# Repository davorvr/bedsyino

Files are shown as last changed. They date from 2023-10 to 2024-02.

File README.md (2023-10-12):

# BeDSyino

#### What is it?

The **[BeDSy (Behaviour-recording Device Synchroniser)](https://github.com/davorvr/bedsy)** is a platform for hardware triggering and synchronisation of equipment for laboratory animal behavioural monitoring. For more information about the BeDSy platform, check the **[BeDSy repository](https://github.com/davorvr/bedsy)**.

The platform consists of two components: the **[BeDSy Python package](https://github.com/davorvr/bedsy)**, which interfaces with the **BeDSyino**, a hardware platform which sends custom trigger signals to animal behaviour-monitoring devices.

The BeDSyino is based on the [Teensy 4.0](https://www.pjrc.com/store/teensy40.html) platform (with plans to migrate to the Teensy 4.1) and [Teensyduino](https://www.pjrc.com/teensy/teensyduino.html).

#### Current state

The [BeDSyino](https://github.com/davorvr/bedsyino) is still cooking. While the code is mostly complete, only a single hand-soldered, protoboard-based prototype has been developed thus far. A modular, extensible hardware platform is currently in the works and hardware files will be uploaded as soon as it's ready. The `.ino` file contains a lot of (hopefully) helpful comments, but more work on the documentation is necessary.

*TO DO - expand*

#### License

The code is distributed under GPLv3.

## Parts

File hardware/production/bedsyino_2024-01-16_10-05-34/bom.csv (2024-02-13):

Designator | Footprint | Quantity | Value | LCSC Part #
C1 | 1206 | 1 | 10uF | C97954
C2, C3, C4, C5, C6 | 0805 | 5 | 0.1uF | C49678
R1, R10, R2, R3, R4, R5, R6, R7, R8, R9 | 0805 | 10 | 10k | C100047
U2 | SOIC-20W_7.5x12.8mm_P1.27mm | 1 | CD74HCT241M96 | C2860724
U3, U4, U5, U6 | SOIC8-N_MC_MCH | 4 | TC4427AVOA | C624944

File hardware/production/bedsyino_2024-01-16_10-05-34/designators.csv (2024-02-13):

C1:1
C2:1
C3:1
C4:1
C5:1
C6:1
J1:1
J10:1
J11:1
J2:1
J3:1
J4:1
J5:1
J6:1
J7:1
J8:1
J9:1
JP1:1
JP10:1
JP11:1
JP12:1
JP13:1
JP14:1
JP15:1
JP16:1
JP17:1
JP18:1
JP19:1
JP2:1
JP20:1
JP21:1
JP22:1
JP23:1
JP24:1
JP25:1
JP26:1
JP27:1
JP28:1
JP3:1
JP4:1
JP5:1
JP6:1
JP7:1
JP8:1
JP9:1
R1:1
R10:1
R2:1
R3:1
R4:1
R5:1
R6:1
R7:1
R8:1
R9:1
REF**:3
U1:1
U2:1
U3:1
U4:1
U5:1
U6:1

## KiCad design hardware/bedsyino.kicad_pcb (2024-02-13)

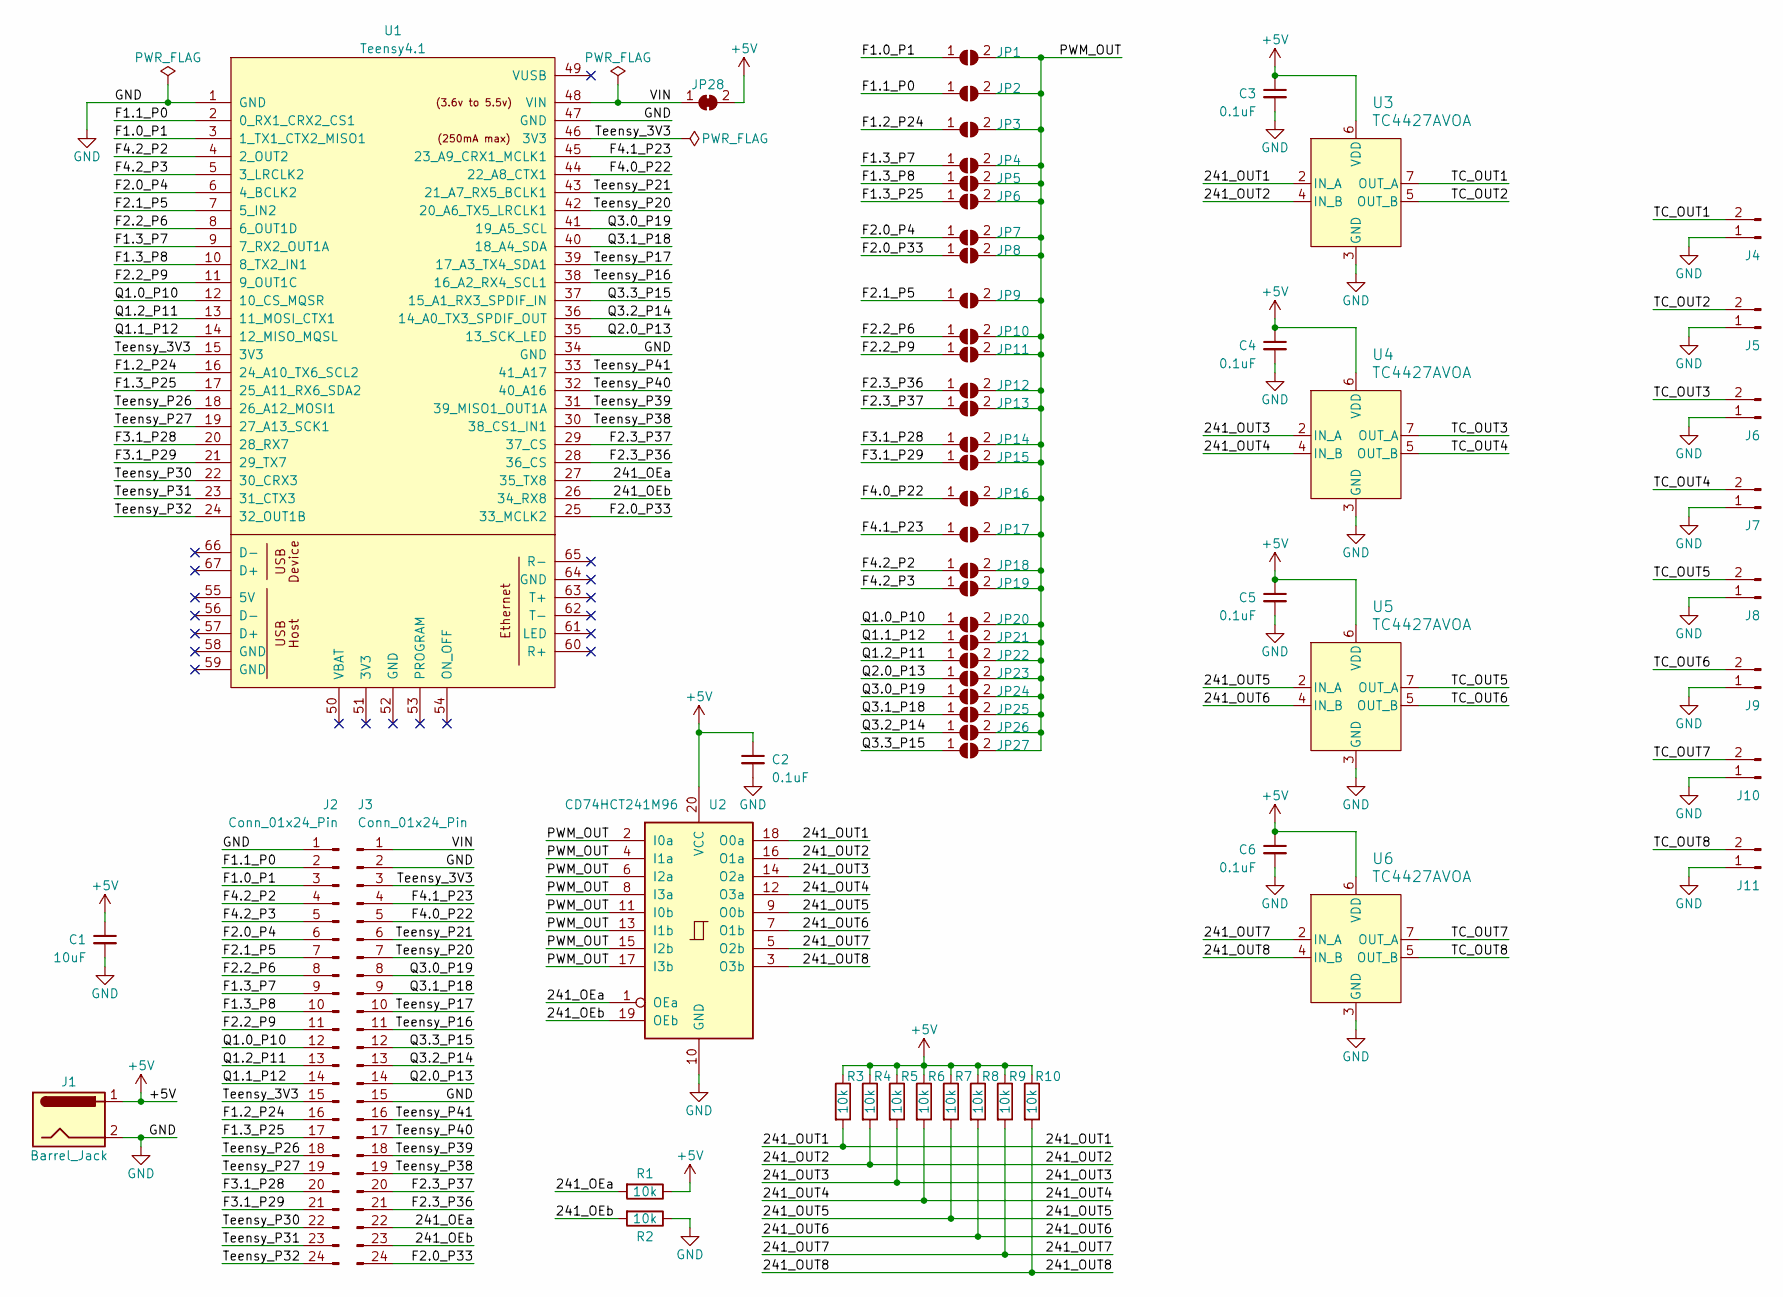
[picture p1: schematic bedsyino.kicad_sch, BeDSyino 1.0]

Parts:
C1: 10uF; C_1206_3216Metric; LCSC Part # C97954
C2, C3, C4, C5, C6: 0.1uF; C_0805_2012Metric; LCSC Part # C49678
J1: Barrel_Jack; BarrelJack_Horizontal
J2, J3: Conn_01x24_Pin; PinHeader_1x24_P2.54mm_Vertical
J4, J5, J6, J7, J8, J9, J10, J11: Conn_01x02_Pin; Molex_KK-254_AE-7395-02_1x02_P2.54mm_Horizontal
JP1: F1.0 P1; SolderJumper-2_P1.3mm_Open_TrianglePad1.0x1.5mm
JP2: F1.1 P0; SolderJumper-2_P1.3mm_Open_TrianglePad1.0x1.5mm
JP3: F1.2 P24; SolderJumper-2_P1.3mm_Open_TrianglePad1.0x1.5mm
JP4: F1.3 P7; SolderJumper-2_P1.3mm_Open_TrianglePad1.0x1.5mm
JP5: F1.3 P8; SolderJumper-2_P1.3mm_Open_TrianglePad1.0x1.5mm
JP6: F1.3 P25; SolderJumper-2_P1.3mm_Open_TrianglePad1.0x1.5mm
JP7: F2.0 P4; SolderJumper-2_P1.3mm_Open_TrianglePad1.0x1.5mm
JP8: F2.0 P33; SolderJumper-2_P1.3mm_Open_TrianglePad1.0x1.5mm
JP9: F2.1 P5; SolderJumper-2_P1.3mm_Open_TrianglePad1.0x1.5mm
JP10: F2.2 P6; SolderJumper-2_P1.3mm_Open_TrianglePad1.0x1.5mm
JP11: F2.2 P9; SolderJumper-2_P1.3mm_Open_TrianglePad1.0x1.5mm
JP12: F2.3 P36; SolderJumper-2_P1.3mm_Open_TrianglePad1.0x1.5mm
JP13: F2.3 P37; SolderJumper-2_P1.3mm_Open_TrianglePad1.0x1.5mm
JP14: F3.1 P28; SolderJumper-2_P1.3mm_Open_TrianglePad1.0x1.5mm
JP15: F3.1 P29; SolderJumper-2_P1.3mm_Open_TrianglePad1.0x1.5mm
JP16: F4.0 P22; SolderJumper-2_P1.3mm_Open_TrianglePad1.0x1.5mm
JP17: F4.1 P23; SolderJumper-2_P1.3mm_Open_TrianglePad1.0x1.5mm
JP18: F4.2 P2; SolderJumper-2_P1.3mm_Open_TrianglePad1.0x1.5mm
JP19: F4.2 P3; SolderJumper-2_P1.3mm_Open_TrianglePad1.0x1.5mm
JP20: Q1.0 P10; SolderJumper-2_P1.3mm_Open_TrianglePad1.0x1.5mm
JP21: Q1.1 P12; SolderJumper-2_P1.3mm_Open_TrianglePad1.0x1.5mm
JP22: Q1.2 P11; SolderJumper-2_P1.3mm_Open_TrianglePad1.0x1.5mm
JP23: Q2.0 P13; SolderJumper-2_P1.3mm_Open_TrianglePad1.0x1.5mm
JP24: Q3.0 P19; SolderJumper-2_P1.3mm_Open_TrianglePad1.0x1.5mm
JP25: Q3.1 P18; SolderJumper-2_P1.3mm_Open_TrianglePad1.0x1.5mm
JP26: Q3.2 P14; SolderJumper-2_P1.3mm_Open_TrianglePad1.0x1.5mm
JP27: Q3.3 P15; SolderJumper-2_P1.3mm_Open_TrianglePad1.0x1.5mm
JP28: PWR SELECT; SolderJumper-2_P1.3mm_Bridged2Bar_Pad1.0x1.5mm
R1, R2, R3, R4, R5, R6, R7, R8, R9, R10: 10k; R_0805_2012Metric; LCSC Part # C100047
U1: Teensy4.1; Teensy41
U2: CD74HCT241M96; SOIC-20W_7.5x12.8mm_P1.27mm; LCSC Part # C2860724
U3, U4, U5, U6: TC4427AVOA; SOIC8-N_MC_MCH; LCSC Part # C624944

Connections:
+5V: C1.1, C2.1, C3.1, C4.1, C5.1, C6.1, J1.1, JP28.2 (B), R1.1, R3.1, R4.1, R5.1, R6.1, R7.1, R8.1, R9.1, R10.1, U2.20 (VCC), U3.6 (VDD), U4.6 (VDD), U5.6 (VDD), U6.6 (VDD)
/241_OEa: J3.22, R1.2, U1.27 (35_TX8), U2.1 (OEa)
/241_OEb: J3.23, R2.2, U1.26 (34_RX8), U2.19 (OEb)
/241_OUT1: R3.2, U2.18 (O0a), U3.2 (IN_A)
/241_OUT2: R4.2, U2.16 (O1a), U3.4 (IN_B)
/241_OUT3: R5.2, U2.14 (O2a), U4.2 (IN_A)
/241_OUT4: R6.2, U2.12 (O3a), U4.4 (IN_B)
/241_OUT5: R7.2, U2.9 (O0b), U5.2 (IN_A)
/241_OUT6: R8.2, U2.7 (O1b), U5.4 (IN_B)
/241_OUT7: R9.2, U2.5 (O2b), U6.2 (IN_A)
/241_OUT8: R10.2, U2.3 (O3b), U6.4 (IN_B)
/F1.0_P1: J2.3, JP1.1 (A), U1.3 (1_TX1_CTX2_MISO1)
/F1.1_P0: J2.2, JP2.1 (A), U1.2 (0_RX1_CRX2_CS1)
/F1.2_P24: J2.16, JP3.1 (A), U1.16 (24_A10_TX6_SCL2)
/F1.3_P7: J2.9, JP4.1 (A), U1.9 (7_RX2_OUT1A)
/F1.3_P8: J2.10, JP5.1 (A), U1.10 (8_TX2_IN1)
/F1.3_P25: J2.17, JP6.1 (A), U1.17 (25_A11_RX6_SDA2)
/F2.0_P4: J2.6, JP7.1 (A), U1.6 (4_BCLK2)
/F2.0_P33: J3.24, JP8.1 (A), U1.25 (33_MCLK2)
/F2.1_P5: J2.7, JP9.1 (A), U1.7 (5_IN2)
/F2.2_P6: J2.8, JP10.1 (A), U1.8 (6_OUT1D)
/F2.2_P9: J2.11, JP11.1 (A), U1.11 (9_OUT1C)
/F2.3_P36: J3.21, JP12.1 (A), U1.28 (36_CS)
/F2.3_P37: J3.20, JP13.1 (A), U1.29 (37_CS)
/F3.1_P28: J2.20, JP14.1 (A), U1.20 (28_RX7)
/F3.1_P29: J2.21, JP15.1 (A), U1.21 (29_TX7)
/F4.0_P22: J3.5, JP16.1 (A), U1.44 (22_A8_CTX1)
/F4.1_P23: J3.4, JP17.1 (A), U1.45 (23_A9_CRX1_MCLK1)
/F4.2_P2: J2.4, JP18.1 (A), U1.4 (2_OUT2)
/F4.2_P3: J2.5, JP19.1 (A), U1.5 (3_LRCLK2)
/PWM_OUT: JP1.2 (B), JP2.2 (B), JP3.2 (B), JP4.2 (B), JP5.2 (B), JP6.2 (B), JP7.2 (B), JP8.2 (B), JP9.2 (B), JP10.2 (B), JP11.2 (B), JP12.2 (B), JP13.2 (B), JP14.2 (B), JP15.2 (B), JP16.2 (B), JP17.2 (B), JP18.2 (B), JP19.2 (B), JP20.2 (B), JP21.2 (B), JP22.2 (B), JP23.2 (B), JP24.2 (B), JP25.2 (B), JP26.2 (B), JP27.2 (B), U2.2 (I0a), U2.4 (I1a), U2.6 (I2a), U2.8 (I3a), U2.11 (I0b), U2.13 (I1b), U2.15 (I2b), U2.17 (I3b)
/Q1.0_P10: J2.12, JP20.1 (A), U1.12 (10_CS_MQSR)
/Q1.1_P12: J2.14, JP21.1 (A), U1.14 (12_MISO_MQSL)
/Q1.2_P11: J2.13, JP22.1 (A), U1.13 (11_MOSI_CTX1)
/Q2.0_P13: J3.14, JP23.1 (A), U1.35 (13_SCK_LED)
/Q3.0_P19: J3.8, JP24.1 (A), U1.41 (19_A5_SCL)
/Q3.1_P18: J3.9, JP25.1 (A), U1.40 (18_A4_SDA)
/Q3.2_P14: J3.13, JP26.1 (A), U1.36 (14_A0_TX3_SPDIF_OUT)
/Q3.3_P15: J3.12, JP27.1 (A), U1.37 (15_A1_RX3_SPDIF_IN)
/TC_OUT1: J4.2, U3.7 (OUT_A)
/TC_OUT2: J5.2, U3.5 (OUT_B)
/TC_OUT3: J6.2, U4.7 (OUT_A)
/TC_OUT4: J7.2, U4.5 (OUT_B)
/TC_OUT5: J8.2, U5.7 (OUT_A)
/TC_OUT6: J9.2, U5.5 (OUT_B)
/TC_OUT7: J10.2, U6.7 (OUT_A)
/TC_OUT8: J11.2, U6.5 (OUT_B)
/Teensy_3V3: J2.15, J3.3, U1.15 (3V3), U1.46 (3V3)
/Teensy_P16: J3.11, U1.38 (16_A2_RX4_SCL1)
/Teensy_P17: J3.10, U1.39 (17_A3_TX4_SDA1)
/Teensy_P20: J3.7, U1.42 (20_A6_TX5_LRCLK1)
/Teensy_P21: J3.6, U1.43 (21_A7_RX5_BCLK1)
/Teensy_P26: J2.18, U1.18 (26_A12_MOSI1)
/Teensy_P27: J2.19, U1.19 (27_A13_SCK1)
/Teensy_P30: J2.22, U1.22 (30_CRX3)
/Teensy_P31: J2.23, U1.23 (31_CTX3)
/Teensy_P32: J2.24, U1.24 (32_OUT1B)
/Teensy_P38: J3.19, U1.30 (38_CS1_IN1)
/Teensy_P39: J3.18, U1.31 (39_MISO1_OUT1A)
/Teensy_P40: J3.17, U1.32 (40_A16)
/Teensy_P41: J3.16, U1.33 (41_A17)
/VIN: J3.1, JP28.1 (A), U1.48 (VIN)
GND: C1.2, C2.2, C3.2, C4.2, C5.2, C6.2, J1.2, J2.1, J3.2, J3.15, J4.1, J5.1, J6.1, J7.1, J8.1, J9.1, J10.1, J11.1, R2.1, U1.1 (GND), U1.34 (GND), U1.47 (GND), U2.10 (GND), U3.3 (GND), U4.3 (GND), U5.3 (GND), U6.3 (GND)

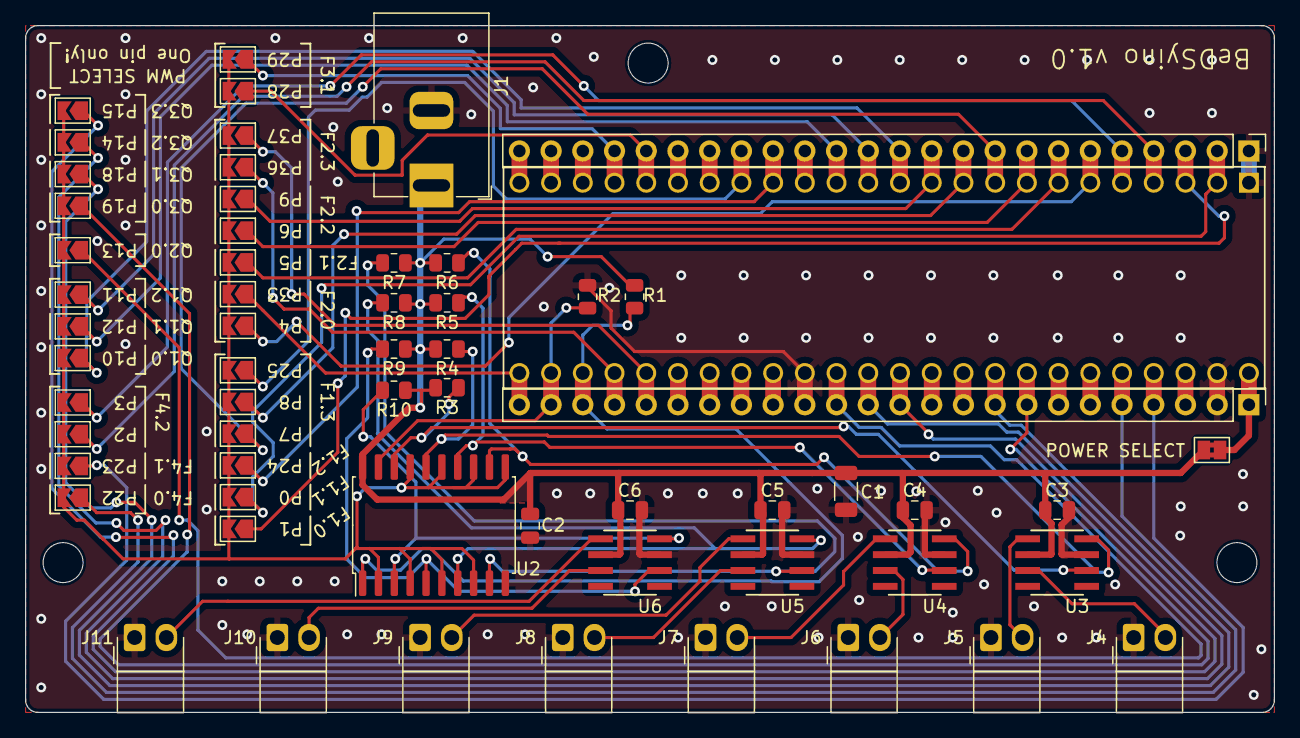
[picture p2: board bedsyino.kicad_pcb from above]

Board: 2 copper layers, 100.0 x 55.0 mm, 61 parts (0 on the bottom side), 63 nets.

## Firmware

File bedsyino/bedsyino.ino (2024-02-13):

/* TODO: Update this block comment for Bedsyino v1.0 (this refers to the prototype)
 * 
 * This code intends to provide a flexible triggering device for synchronising multiple devices
 * that need to operate concurrently. Currently, it outputs two different kinds of signals:
 *      - square wave to trigger many Basler cameras (1 pulse = 1 frame)
 *      - active-low signal for the DIN input of a single AviSoft UltraSound Gate
 *        (can be used to trigger all connected ultrasonic microphones simultaneously)
 * Block diagram:
 *      ________
 *     |        |      _________
 *     |        |     |         |
 *     | Teensy |---->|         |----->Cam 1 connector
 *     |  4.0   |     |         |----->Cam 2 connector
 *     |        |     | 74HC244 |----->...
 *     |        |     |         |----->USG connector
 *     |________|     |_________|
 *
 * The 74HC244 serves as a line buffer. It's powered by the USB 5V line, and pulls the signal
 * lines of the devices high or low based on input from the Teensy. It also gets two extra "ENABLE"
 * inputs from the Teensy - turning these HIGH switches the 244's pins from active high or low
 * to high impedance (meaning it will stop actively sending a signal). This is useless for now,
 * but might come in handy some time in the future. For more info, check the 74HC244's datasheet.
 *
 * The device accepts "s" to start and "x" to stop via USB serial. It also automatically stops
 * for a user-defined period of time, and restarts, to enable rollover of logs into a new file.
 * When any of these events happens, a message is send with a machine-scannable code in square brackets.
 * 
 * /TODO
 */
#define PIN_USG_OUT 6
#define PIN_BASLER_OUT 9
#define PIN_ENABLE_1 35
#define PIN_ENABLE_2 34

/* USER CONFIG */
// in milliseconds
const unsigned long rollover_period = 60 * 1000;
const unsigned long rollover_delay = 1000;
bool running = false;
/* END USER CONFIG */

char serial_input;

/*
 * Since the cameras need a square wave signal, PWM (analogWrite) is used to produce it. However,
 * when a PWM signal turns on, it starts at a random point in the cycle. Therefore, it is best
 * to use the same PWM peripheral for all devices - see Teensy docs. All pins connected to the
 * same interal PWM peripheral will share frequencies and be synchronised in phase regardless of
 * the duty cycle, so for a continuous signal, we just set the USG cycle to always on (which is
 * 4096 for 12-bit PWM - 2^12 = 4096). See also: https://docs.arduino.cc/learn/microcontrollers/analog-output
 */
// Turn the signals on
void signals_on() {
  analogWrite(PIN_USG_OUT, 4096); // 4096 is always on
  // 1024 is 1024/4096=25% duty cycle - it just needs to stay high
  // for long enough, and then low for long enough for the camera
  // to recognise it. 25% for freqs like 30-50 Hz/FPS is just fine.
  analogWrite(PIN_BASLER_OUT, 1024);
  //digitalWrite(PIN_ENABLE_1, LOW);
  //digitalWrite(PIN_ENABLE_2, LOW);
  digitalWrite(LED_BUILTIN, HIGH);
}

void signals_off() {
  analogWrite(PIN_USG_OUT, 0);
  analogWrite(PIN_BASLER_OUT, 0);
  //digitalWrite(PIN_ENABLE_1, HIGH);
  //digitalWrite(PIN_ENABLE_2, HIGH);
  digitalWrite(LED_BUILTIN, LOW);
}

// function to report time until rollover upon request from the serial port (command: "?")
void report_state(unsigned long timer, unsigned long timeout) {
  if (running) {
    Serial.printf("Running. Timeout in: %lu s. Timeout period: %lu s\n", (timeout - timer) / 1000, timeout / 1000);
  } else {
    Serial.println("Not running.");
  }
}

void outputs_enable() {
  digitalWrite(PIN_ENABLE_1, LOW);
  digitalWrite(PIN_ENABLE_2, HIGH);
}

void outputs_disable() {
  digitalWrite(PIN_ENABLE_1, HIGH);
  digitalWrite(PIN_ENABLE_2, LOW);
}

void setup() {
  // initialize ENABLE pins and use them to disable the 241's output
  pinMode(PIN_ENABLE_1, OUTPUT);
  pinMode(PIN_ENABLE_2, OUTPUT);
  outputs_disable();

  /* set up the PWM internal peripheral */
  // 12 bits resolution - PWM values from 0 (always off) to
  // 4096 (always on). values in between set the duty cycle
  analogWriteResolution(12); 
  // set 30 Hz frequency. this is important for the camera, but in reality,
  // the USG_OUT will just be always on or always off.
  // we still use analogWrite for USG_OUT so it's synchronised with BASLER_OUT
  analogWriteFrequency(PIN_USG_OUT, 30);
  analogWriteFrequency(PIN_BASLER_OUT, 30);
  // initialize the LED pin on the Teensy board
  pinMode(LED_BUILTIN, OUTPUT);

  // enable the 241's output now that everything is set up
  outputs_enable();

  // start with signals on or off based on the initial setting of the "running" flag
  if (running) signals_on();
  else signals_off();
}

void loop() {
  // initialise the timer for the rollover period. for more info on how it's used,
  // see here: https://www.pjrc.com/teensy/td_timing_elaspedMillis.html (Teensy-specific)
  elapsedMillis waiting;
  // if we're not running, or if we're waiting for the rollover period to elapse
  // (this is most of the time), we wait for a command via serial.
  while ((waiting < rollover_period) || (!running)) {
    // we wait for a command via serial
    if (Serial.available()) {
      serial_input = Serial.read();
      while (Serial.available()) Serial.read();
      // "s" command - START
      if (serial_input == 's') {
        signals_on();
        Serial.println("[START] Signals on. Resetting the timer.");
        running = true;
        waiting = 0; // timer reset
      }
      // "x" command - STOP completely and permanently
      if (serial_input == 'x') {
        signals_off();
        Serial.println("[STOP_PERMANENT] Signals off.");
        running = false;
      }
      // "?" command - get timing status while the device is running
      if (serial_input == '?') {
        report_state(waiting, rollover_period);
      }
    }
    delay(1);
  }
  // this part executes only in between rollovers:
  waiting = 0; // timer reset
  signals_off(); // turn off signals
  Serial.println("[STOP_ROLLOVER] Turning signals off for 1 second..."); // inform the user
  // wait a bit until we restart so the user has time to do whatever in between rollovers
  while (waiting < rollover_delay);
  // finally, start the signal and inform the user
  signals_on(); 
  Serial.println("[START] Signals on. (automatic)");
}

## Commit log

2024-02-13 added PCB design for v1.0
    [bedsyino.kicad_pcb, bedsyino.kicad_sch, bom.csv, designators.csv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]
2024-02-13 Updated code for Bedsyino v1.0 test
    Code still specific for one use case, main block comment still not updated
